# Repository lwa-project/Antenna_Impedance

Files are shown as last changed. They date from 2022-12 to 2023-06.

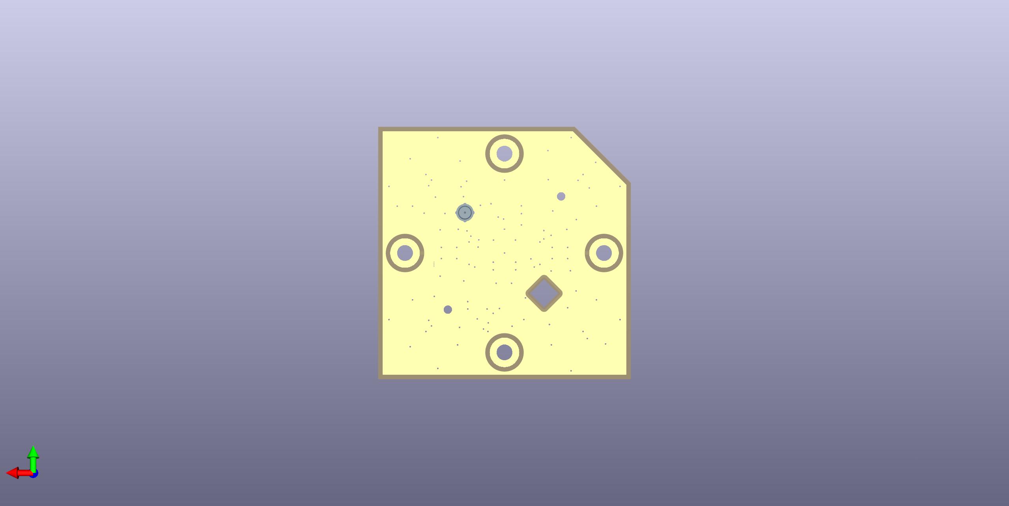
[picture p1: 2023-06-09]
Test Fixtures/LWA Active Test Fixture 2022/Output Files/3D Views/Bottom View LWA Active Test 2022.jpg

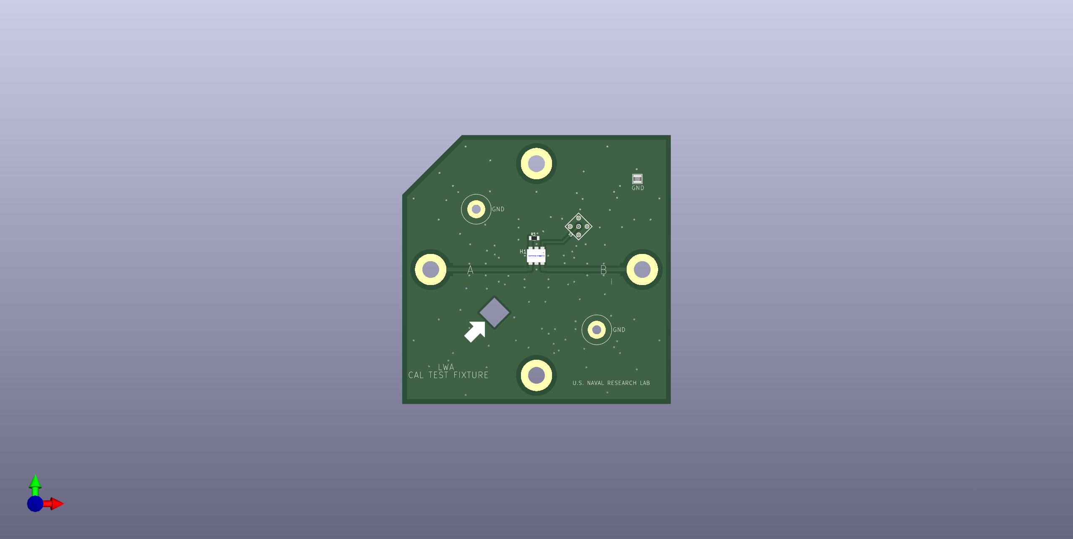
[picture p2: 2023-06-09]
Test Fixtures/LWA Active Test Fixture 2022/Output Files/3D Views/Top View LWA Active Test 2022.jpg

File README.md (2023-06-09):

Antenna_Impedance
===================
  

Description
-----------
Collection of scripts and files dealing with the LWA antenna impedance.

In the main directory are the general scripts:
* compute_IME.py: Reads in a single .s1p file containing antenna reflection coefficient data and computes the IME 
* plot_IME.py: Plots the output from computeIME.py along with the model IME from antenna simulations
* compute_IMF.py: Reads in a .npz file output by read_FEE_S_params.py and a collection of antenna .s2p files to compute the Impedance Mismatch Factor (IMF)
* plot_S_params.py: Takes in a collection of .s2p files and plots the full set of S-parameters for each antenna. Used to make the dipole-dipole measurement plots.
* plot_cross_coupling.py: Takes in a collection of .s2p files from an antenna-antenna cross coupling measurement and plots S12 and S21 for each of the four possible polarization permutations. 

Data Files
----------
In the Data/ directory there is a collection of various data files with their associated documentation.
Files include:
* BurnsZ.txt: Model IME from old antenna simulations
* A-NS_AntennaImpedance_062222.s1p: Antenna Impedance for A (N/S) polarization taken on 06/22/2022 at Whitham Reeve's house in Alaska
* B-EW_AntennaImpedance_062222.s1p: Antenna Impedance for B (E/W) polarization taken on 06/22/2022 at Whitham Reeve's house in Alaska
* A collection of dipole-dipole and antenna-antenna .s2p measurement files taken at the New Mexico stations (See "LWA_NM_Measurements_and_Procedures.pdf" for more information)

FEE
---
The Data/FEE/ directory contains:
* A collection of .s2p files which contains S-parameter measurements with the HX62A of the FEE Test Fixture de-embedded.
* read_FEE_S_params.py: A script to read both the .s1p and .s2p files and write out proper S-pramaters (S11 with HX62A de-embdedd, correct S21 and S12, and S22).
* plot_FEE_Gain.py: A script to plot the FEE Gain files which are output by read_FEE_S_params.py

Example
-------
The following is a short example which shows how to generate the IMF correction for LWA data, which requires both LWA antenna S11 measurements and FEE S11 measurements.
The FEE S11 data with the HX62A de-embedded are located in `Data/FEE/S1P/`. The single antenna measurements for each station are located in the named directories in the `Data/` directory
under `Dipole-Dipole/` (e.g. the LWA-SV measurements are in `Data/LWA-SV/Dipole-Dipole/`.

First, the FEE S-parameters with the HX62A de-embedded have to be collected into a single .npz file. To do this, use `Data/FEE/read_FEE_S_params.py` for both polarizations:
```
python3 read_FEE_S_params.py -ns S2P/*A*
```
and
```
python3 read_FEE_S_params.py -ns S2P/*B*
```
This creates two files `FEE_S11_NS.npz` and `FEE_S11_EW.npz`, respectively. Finally, to compute the IMF correction using LWA1 antenna measurements and FEE S11 measurements use `compute_IMF.py`
for each polarization via
```
python3 compute_IMF.py -ns Data/FEE/FEE_S11_NS.npz Data/LWA1/Dipole-Dipole/*
```
and
```
python3 compute_IMF.py -ns Data/FEE/FEE_S11_EW.npz Data/LWA1/Dipole-Dipole/*
```
This creates two files named `IMF_NS.txt` and `IMF_EW.txt`, respectively, which contain the IMF as a function of frequency along with the $16^{th}$ and $84^{th}$ percentile uncertainty bounds.

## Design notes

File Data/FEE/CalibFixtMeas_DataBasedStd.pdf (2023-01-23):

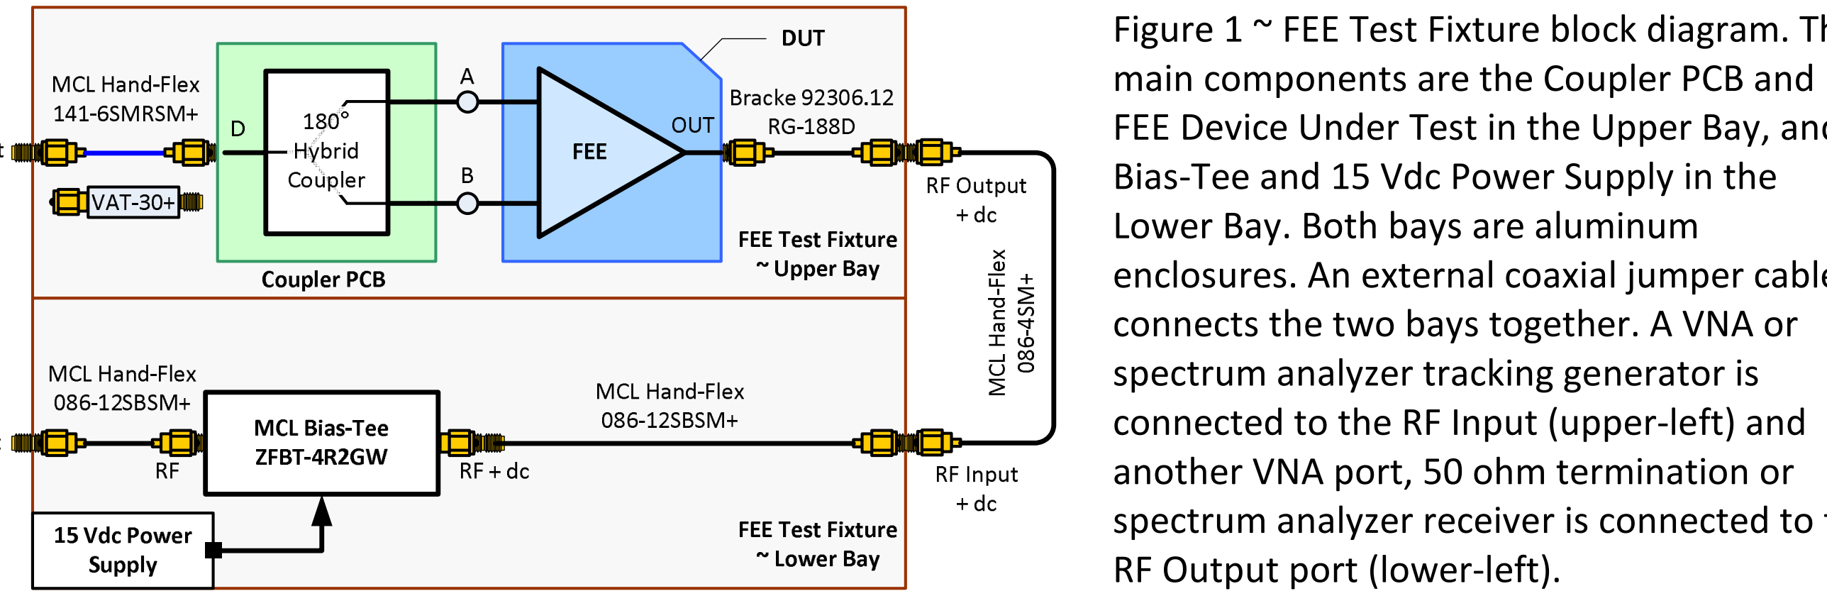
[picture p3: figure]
main components are the Coupler PCB and; Bias-Tee and 15 Vdc Power Supply in the Lower Bay. Both bays are aluminum; spectrum analyzer tracking generator is; another VNA port, 50 ohm termination or; RF Output port (lower-left).
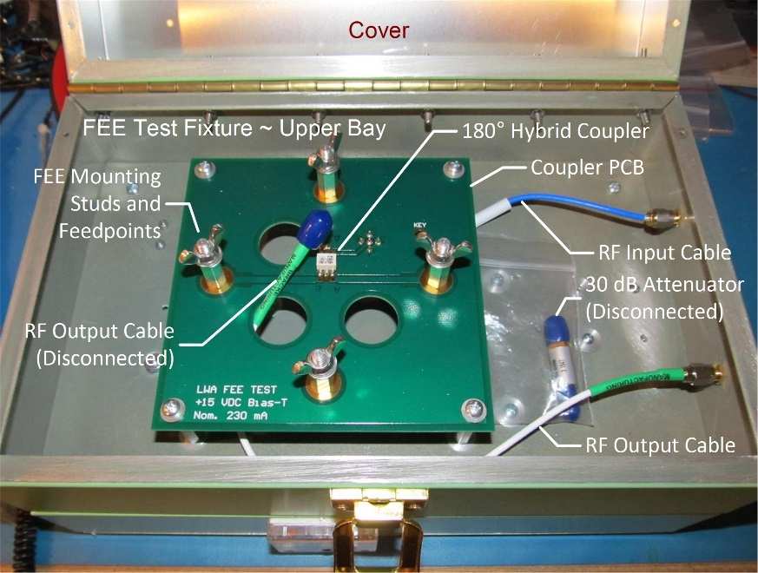
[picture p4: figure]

File: CalibFixtMeas_DataBasedStd.docx, Page 1

Calibration Fixture Measurements & Associated Data-Based Standards

The FEE Test Fixture (figures 1 and 2) is designed for measurements of the LWA Antenna Front End Electronics (FEE). To allow connection of the unbalanced 50 ohm port of a vector network analyzer (VNA) or spectrum analyzer tracking generator output to the balanced feedpoints of the FEE, the FEE Test Fixture includes a Coupler Printed Circuit Board (PCB) with a 180° hybrid coupler that provides the unbalanced to balanced transformation. Unless the hybrid coupler on the Coupler PCB is de-embedded from the measurements of the FEE, the measurements will include the characteristics of both the hybrid coupler and FEE. This paper describes using Data-Based Standards to perform the de-embedding.

The FEE Test Fixture V1 uses the HX62A hybrid coupler on the Coupler PCB, and the FEE Test Fixture V2 uses the AMT-32+ hybrid coupler on the Coupler PCB. All Calibration Fixtures use the AMT-32+ hybrid coupler. For consistency, it is necessary to use the FEE Test Fixture V2 in all measurements described below.

Figure 1 ~ FEE Test Fixture block diagram. The

FEE Device Under Test in the Upper Bay, and

enclosures. An external coaxial jumper cable connects the two bays together. A VNA or

connected to the RF Input (upper-left) and

spectrum analyzer receiver is connected to the

Figure 2.a ~ FEE Test Fixture Upper Bay showing the Coupler PCB and input and output cables. The RF Input cable connects to the difference port of the 180° hybrid coupler. The A and B ports of the hybrid coupler connect to the FEE Mounting Studs, which also serve as Feedpoints. Four studs are seen on the Coupler PCB but only the left and right studs are used during testing. The RF Output cable connects to the FEE output port. The 30 dB attenuator, shown loose in a reclosable bag, is used when measuring the FEE gain with a spectrum analyzer and tracking generator.

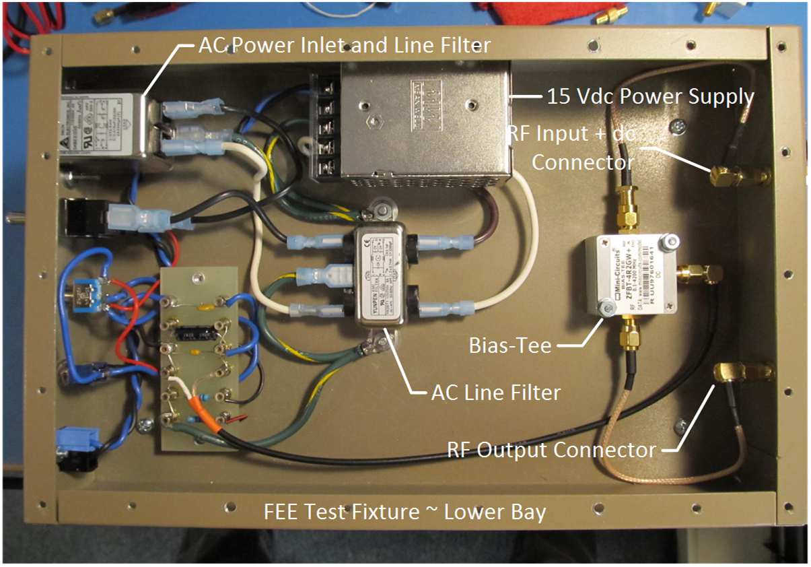
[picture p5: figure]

File: CalibFixtMeas_DataBasedStd.docx, Page 2

Figure 2.b ~ FEE Test Fixture Lower Bay showing the dc power supply, bias-tee and ac line filter components. Two stages of ac line filtering are used, and the ac power inlet is fused. Other components are current limiting resistors for the power indicating LEDs, and dc filter capacitors. The FEE Test Fixture also has selection switches for the internal or an external power source. Not visible in this image is a dc ammeter for measuring FEE load current.

VNAs are used to measure four S-parameters S11, S21, S12 and S22 but, here, we are concerned only with the S11 reflection coefficient measured at the FEE feedpoints. All VNAs require calibration prior to use. The most common VNA calibration methods involve Open, Short and Load mechanical calibration standards. A set of commercial calibration standards is called a Calibration Kit (commonly called a Cal Kit). The typical Cal Kit consists of precision coaxial devices characterized by a propagation delay term that accounts for the distance of the open or short from the reference plane of their coaxial connectors and a frequency-dependent polynomial expression that accounts for fringe capacitance in the Open and inductance in the Short standards.

The balanced feedpoint structure of the FEE consists of two annular ring pads (figure 3) that preclude connection of coaxial mechanical calibration standards, so a set of custom Open, Short and Load Calibration Fixtures was designed and fabricated (these are the same standards used for calibration in the LWA Antenna measurements). The Calibration Fixtures (figure 4) include the same type of 180° hybrid coupler and layout as the Coupler PCB described above.

The surface mount technology (SMT) resistors used in the Short and Load Calibration Fixtures are located next to the balanced feedpoints but are not connected to them. The feedpoints are transformed to the unbalanced measurement port by the hybrid coupler. The Open Calibration Fixture has no resistors (infinite resistance) but includes the hybrid coupler and empty SMT pads. Because of the hybrid coupler, the Calibration Fixtures are not easily characterized in the same terms as the commercial mechanical calibration standards described above.

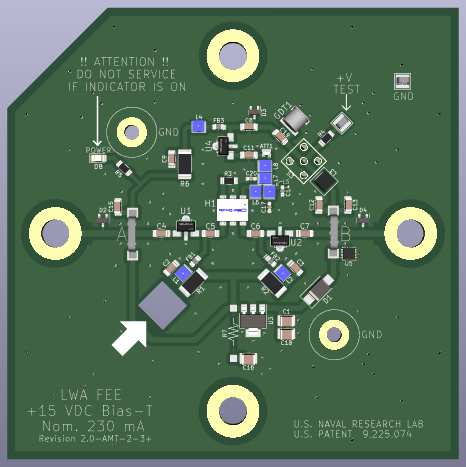
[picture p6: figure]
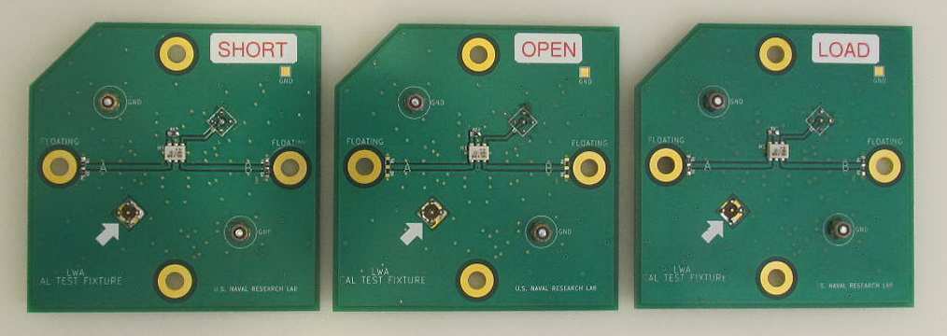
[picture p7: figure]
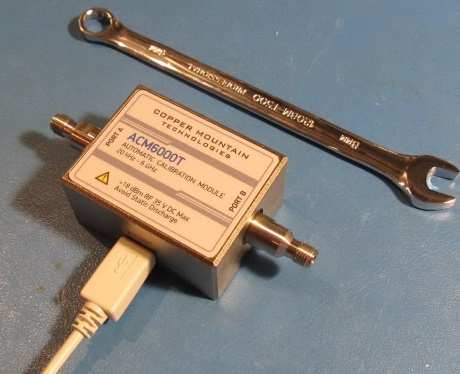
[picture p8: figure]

File: CalibFixtMeas_DataBasedStd.docx, Page 3

Figure 3 ~ CAD image of the FEE. Dimensions are 4.5 x 4.5 in (114.3 x 114.3 mm). The FEE consists of two identical PCBs except for the direction of the SMA connector (the connector pads are seen near the middle of the upper-right quadrant). The PCBs are sandwiched back-to-back to provide a dual assembly. The left and right annular rings are connected to circuitry facing out of the page and the upper and lower annular rings are connected to the circuitry on the other PCB facing into the page. The ring hole diameters are slightly more than ¼ in (6.35 mm). During normal operation, the FEE is mounted to studs in the LWA Antenna central hub. The corner notch (upper-left) ensures proper alignment in the antenna hub. For test purposes, the FEE is mounted in the FEE Test Fixture, which has an identical stud layout that provides connections to the Coupler PCB.

Figure 4 ~ Calibration
Fixtures. Each fixture is a dual assembly of two
identical PCBs. The SMT
pads for the Short and Load resistors are adjacent to the annular rings. The Open
Fixture has pads but no
resistors. All use the AMT-32+ hybrid coupler.

An alternative characterization method involves carefully measuring the S11 reflection coefficients of the Calibration Fixtures and then using those measurements as Data-Base Standards for VNA calibration. In this method, the VNA is used to measure the reflection coefficient of each Calibration Fixture. Ideally, the data base is created by measurements with a metrology-grade VNA that has been calibrated with primary standards in a controlled environment laboratory. As a practical matter, the measurements can be made with a high-quality VNA after it has been calibrated with an Automatic Calibration Module (ACM) (figure 5).

Figure 5 ~ Copper Mountain Technologies USB-controlled ACM6000T-111 Automatic Calibration Module with two ports and SMA-female connectors shown adjacent to an 8 mm wrench. The ACM allows more precise VNA calibration than a mechanical Cal Kit. The device is controlled through a USB port and provides Short, Open, Load and Thru standards in one small package.

The measurement data includes the embedded hybrid coupler in the Calibration Fixtures, which, by proxy, includes the embedded hybrid coupler on the FEE Test Fixture Coupler PCB. This method assumes that the electrical differences between the hybrid couplers used in the Calibration Fixtures and the hybrid coupler in the Coupler PCB are negligible. The Calibration Fixtures and their associated measurement data are then used to

File: CalibFixtMeas_DataBasedStd.docx, Page 4 recalibrate the VNA before measuring an FEE, thus moving the measurement reference plane from the VNA port to the balanced feedpoints of the FEE in the FEE Test Fixture.

The ACM includes the Open, Short, Load, and Through standards in one unit and is controlled by the VNA through a USB port. One advantage of an ACM is that it is individually characterized at the factory, including thermal modeling, allowing more precise VNA calibration than normally possible with mechanical calibration standards. Although mechanical standards are precision devices, they normally are not individually characterized or thermally modeled as is the ACM. The same delays and polynomial coefficients apply to thousands of mechanical calibration standards with the same part number, and the uncertainties in these parameters are unavoidably higher than in an ACM.

Calibration Fixture Data Base Measurements

The Copper Mountain Technologies (CMT) M5045 Vector Network Analyzer and CMT ACM6000T-111 Automatic Calibration Module are used to measure the Calibration Fixtures. The same cable arrangement is used during VNA calibration with the ACM and during measurements of the Calibration Fixtures; thus, the cables are calibrated out. The VNA is setup with the start and stop frequency, number of measurement points, and IF bandwidth. The ACM is automatically detected when the ACM has been connected to a PC USB port.

The ACM is installed at the end of the VNA Test Cable Arrangement on port 1 and a 50 ohm termination is connected to the unused ACM port. A Full 1-Port calibration is initiated. The Test Cable Arrangement includes a 1 m long Test Cable from the VNA and a 6 in long Jumper Cable that is the proxy for the internal RF Input Jumper Cable inside the FEE Test Fixture. This establishes the calibration reference plane at the end of the Test Cable Arrangement. When the automatic calibration has finished, the Calibration Fixtures are installed one by one at the end of the Test Cable Arrangement (figure 6). The S11 parameter measurements are saved as S1P Touchstone files, one each for the Side A Open, Short and Load Calibration Fixtures. The measurements are then repeated for the Side B Open, Short and Load Calibration Fixtures. Two sets of Calibration Fixtures have been constructed and marked with a Red or Yellow dot. All measurements are repeated for both sets of Calibration Fixtures.

The Define STD Data and Define STD CLS functions in the VNA software are then used to define a Data-Based Open, Short and Load from the S1P data files obtained above. Four sets of definitions, or Cal Kits, are produced, one each for Side A and Side B of the Red and Yellow Calibration Fixtures. The definitions are saved to the list of calibration kits available in the VNA. Now, when the VNA is calibrated with these Cal Kits, the hybrid coupler and cables are de-embedded and the measurement reference plane is at the balanced feedpoint of the FEE installed in the FEE Test Fixture.

Several sets of measurements were made to 1) check for hand-capacitance effects, 2) determine if the Calibration Fixtures may be placed on the outside of the FEE Test Fixture and 3) determine if the RF Input Jumper Cable in the FEE Test Fixture may be temporarily replaced with a separate but identical Jumper Cable. Placing the Calibration Fixtures outside the FEE Test Fixture and using an external Jumper Cable minimizes the mechanical disassembly and reassembly of the FEE Test Fixture during the several steps of calibration and FEE measurements. The only hand capacitance effects observed were when the exposed pads or component leads on the Calibration Fixtures were physically touched while holding the fixture, which is not done during

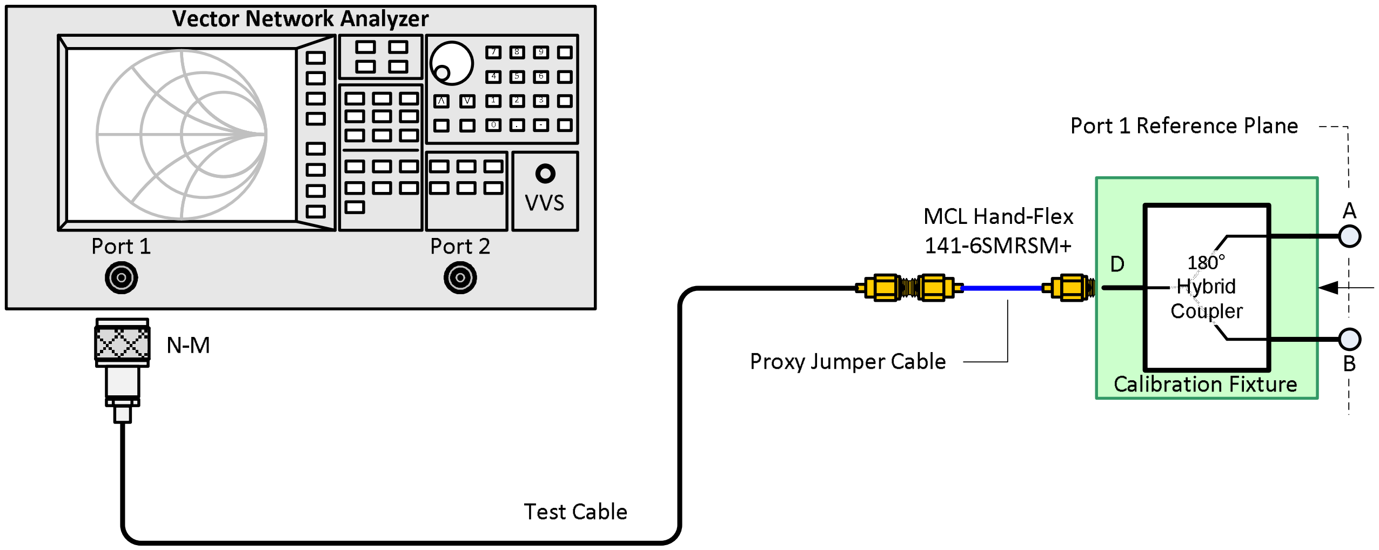
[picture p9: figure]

File: CalibFixtMeas_DataBasedStd.docx, Page 5 calibration or measurements. Also, there were no differences observed between setting the Calibration Fixtures in the FEE Test Fixture and setting them on the test bench external to the FEE Test Fixture with the proxy Jumper Cable.

Figure 6 ~ Calibration setup diagram for Calibration Fixture measurements. Measurements have demonstrated that the Calibration Fixtures may be set outside of the FEE Test Fixture during VNA calibration to minimize mechanical disassembly and reassembly of the FEE Test Fixture. The MCL 141-6SMRSM+ Jumper Cable used in calibration is a proxy for an identical cable used in the FEE Test Fixture.

Procedures:

These procedures produce the data necessary for defining Calibration Fixture Data-Based Standards. These standards apply only to the frequency range 5 to 200 MHz and with an MCL ULC-1M-SMNM+ Test Cable and MCL 141-6SMRSM+ Jumper Cable. Four Cal Kits are produced: Red-A, Red-B, Yellow-A, and Yellow-B:

Step 1 – Initial VNA Calibration:

### 1. Connect the VNA Port 1 Test Cable to the proxy RF Input Jumper Cable (MCL 141-6SMRSM+)

Notes:
a. The proxy cable includes an SMA-female coupler on one end and SMA-male right-angle connector on the other end (same as in the FEE Test Fixture);
b. The combination of the Test Cable and proxy cable is called Test Cable Arrangement

### 2. Setup the VNA for frequencies, number of measurement points and IF bandwidth

3. Connect the ACM Port A to the Test Cable Arrangement and Port B to a 50 ohm termination

### 4. Select AutoCal 1-Port AutoCal (AutoCal is initiated)

### 5. After calibration has finished, the calibration is applied automatically

Step 2 – Measure S11 reflection coefficient of the Calibration Fixtures. This step is required for each of the three Calibration Fixtures:
1. Connect Side A of the Yellow Dot Open Calibration Fixture to the Test Cable Arrangement

### 2. Terminate Side B of the Yellow Dot Open Calibration Fixture with a 50 ohm termination

### 3. Measure 1-Port S11 reflection coefficient on VNA Port 1

### 4. Save measurements as S1P and PNG files

### 5. Repeat steps 1 through 4 for Side B of the Yellow Dot Open Calibration Fixture

### 6. Repeat steps 1 through 5 for Side A and B of the Yellow Dot Short Calibration Fixture

File: CalibFixtMeas_DataBasedStd.docx, Page 6

### 7. Repeat steps 1 through 5 for Side A and B of the Yellow Dot Load Calibration Fixture

### 8. Repeat steps 1 through 7 for the Red Dot Open, Short and Load Calibration Fixtures

Step 3 – Prepare Data-Based Standards for the Calibration Fixtures:
1. Using the S11 measurements of the Open, Short and Load for each set, prepare four Data-Based Standards Cal Kits
2. Define STDs Open, Short and Load, one set of each for Side A and Side B of the Red Dot Calibration Fixtures and one set of each for Side A and Side B of the Yellow Dot Calibration Fixtures

### 3. Define CLSs, Open -F-, Short -F- and Load -F-

File: CalibFixtMeas_DataBasedStd.docx, Page 7

Document Information
Author: Whitham D. Reeve
Revisions: 0.0 (Original draft started, 07 Jan 2023) 0.1 (Major edits, 08 Jan 2023)
0.2 (Updates per tests, 18 Jan 2023) 0.3 (Edited procedures, 19 Jan 2023) 0.4 (Replaced ACM image, 20 Jan 2023) 0.5 (Record, 21 Jan 2023)

Word count: 2892
File size (bytes): 1927712

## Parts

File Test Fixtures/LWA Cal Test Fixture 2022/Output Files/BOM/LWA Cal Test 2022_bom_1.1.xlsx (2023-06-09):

Component | References | MFGR | MPN | Value | Desc | Footprint | Quantity Required | Stock | Stock Date | Tolerance | Unit Cost | Extended
1 | H1 | Mini-Circuits | AMT-32+ | AMT-32+ | Magic Tee, 50 - 200 MHz, 180 deg Hybrid, 50Ω | AMT-2 | 16 | 66 | 03/03/2022 | NA | $13.45 | $215.20
2 | R3 | Vishay Foil Resistors | Y162550R0000B9W | 50R | RES SMD 50 OHM 0.1% 0.3W 1206 | R_1206_3216Metric_Pad1.30x1.75mm_HandSolder | 1 | 2007 | 04/26/2022 | 0.1% | $0.56 | $0.56
3 | R1 R2 R4 R5 | YAGEO | RC1206FR-07100RL | 100R | RES 100 OHM 1% 1/4W 1206 | R_Cal_1206 | 100 | 2220743 | 04/24/2022 | 1% | $0.03 | $3.00
4 | R1 R2 R4 R5 | YAGEO | RC1206JR-070RL | 0R (Shunt) | RES 0 OHM JUMPER 1/4W 1206 | R_Cal_1206 | 100 | 2220743 | 04/24/2022 | NA | $0.02 | $2.00
5 | S3 | Cinch Connectivity Solutions Johnson | 142-0701-201 | TEST | CONN SMA JACK STR 50 OHM PCB | SMA_142-0701-201 | 20 | 40347 | 03/03/2022 | NA | $4.94 | $98.80
6 | TP2 | Harwin Inc | S1751-46R | GND TEST | PC TEST POINT NATURAL | Harwin_TP_S1751-46R | 100 | 157264 | 03/03/2022 | NA | $0.20 | $20.00
 |  |  |  |  |  |  |  |  |  | Total Parts Cost: |  | $339.56
Note: This BOM covers deliverable components needed for both sets of boards.

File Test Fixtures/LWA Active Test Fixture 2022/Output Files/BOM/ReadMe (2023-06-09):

Please see other Project 'LWA Cal Test 2022' for procurement BOM.

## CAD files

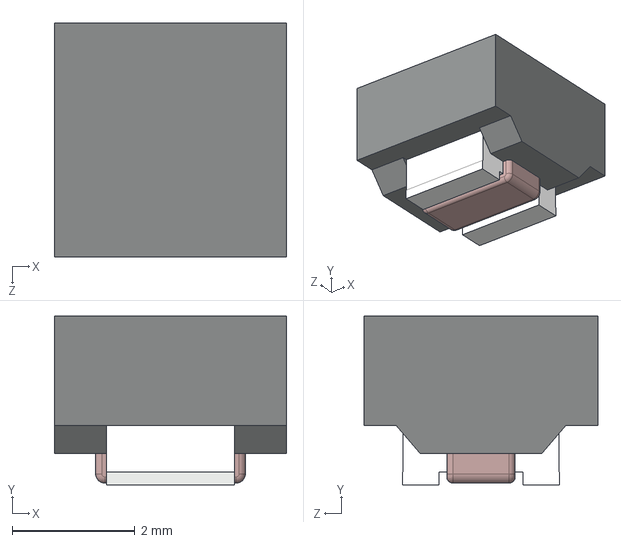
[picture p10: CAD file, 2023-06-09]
Test Fixtures/LWA Active Test Fixture 2022/3D Models/Coilcraft-1008PS.STEP
3.78 x 2.75 x 3.81 mm

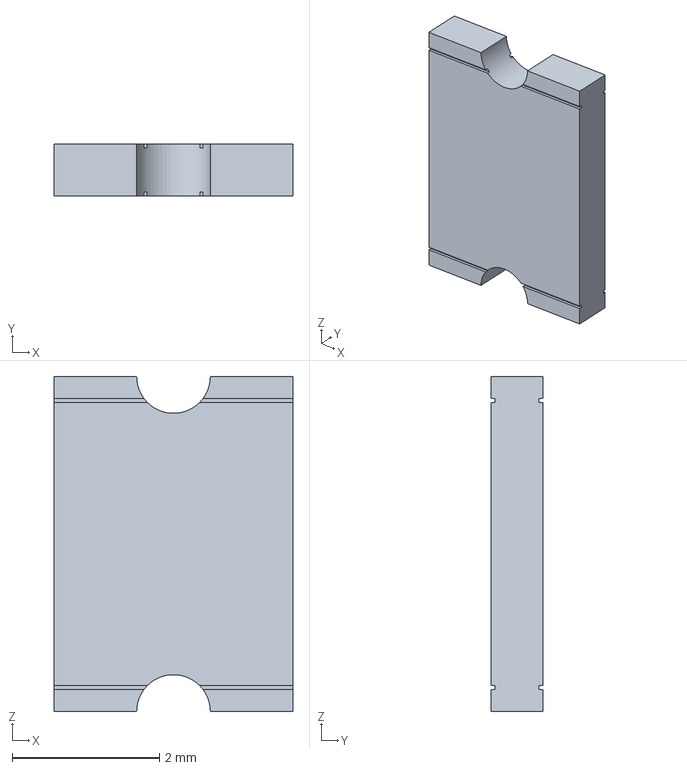
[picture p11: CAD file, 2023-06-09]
Test Fixtures/LWA Active Test Fixture 2022/Project PCB Libraries/3D Models/mf-msmf050.stp
3.24 x 0.7 x 4.55 mm

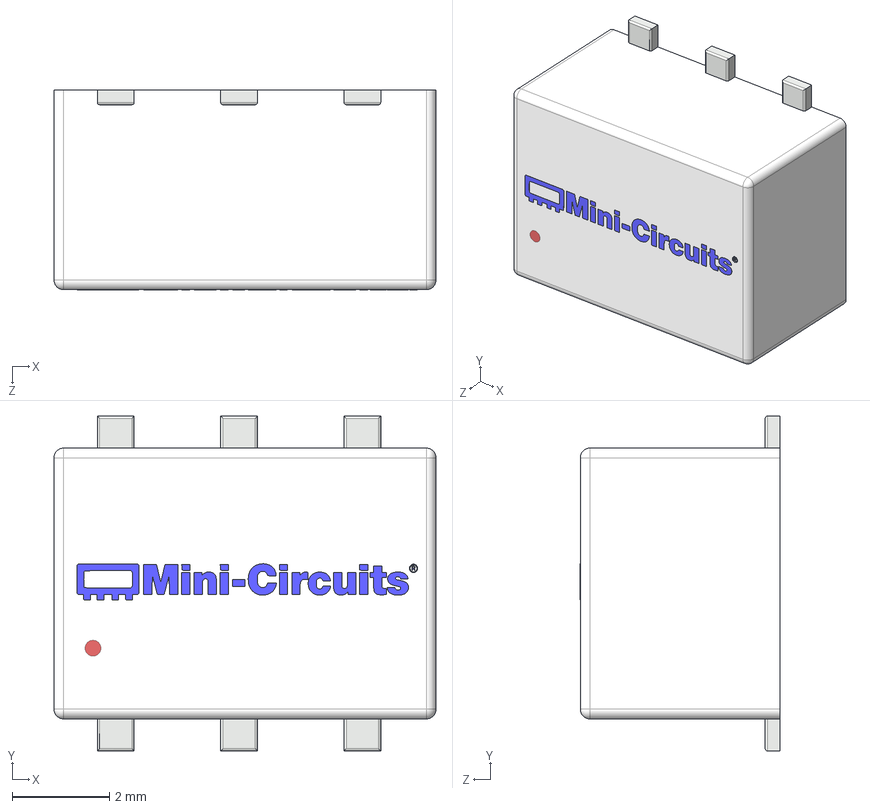
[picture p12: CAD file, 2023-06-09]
Test Fixtures/LWA Cal Test Fixture 2022/3D Models/CD636-1.STEP
7.87 x 6.90 x 4.11 mm

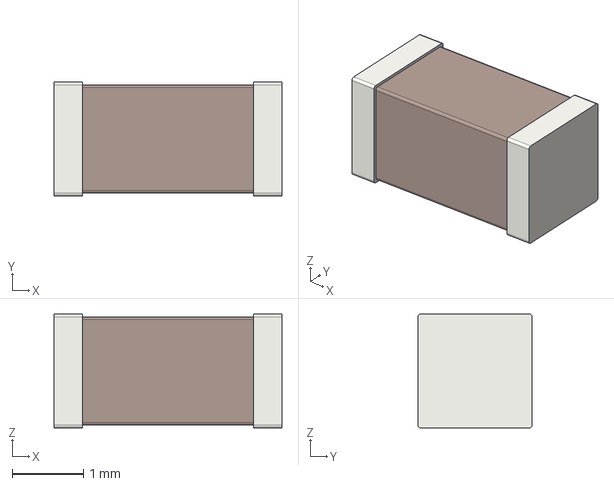
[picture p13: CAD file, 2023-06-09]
Test Fixtures/LWA Cal Test Fixture 2022/Project PCB Libraries/3D Models/C_1206_3216Metric.step
3.20 x 1.60 x 1.60 mm

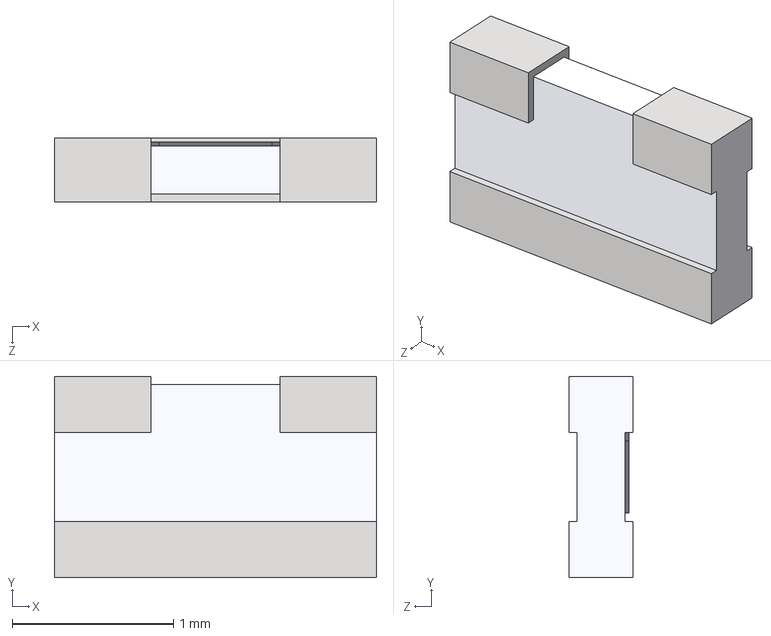
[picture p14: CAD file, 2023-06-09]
Test Fixtures/LWA Active Test Fixture 2022/3D Models/PAT1210.STEP
2.00 x 1.25 x 0.4 mm

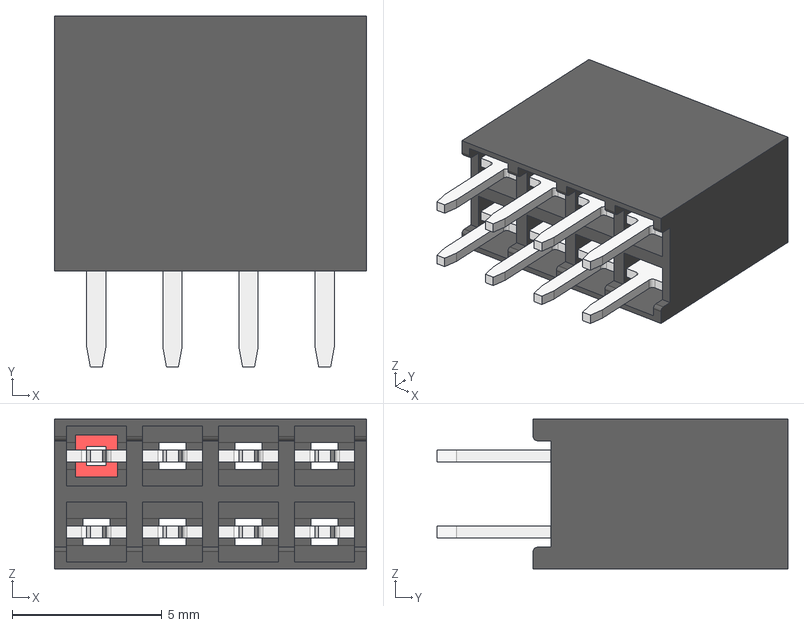
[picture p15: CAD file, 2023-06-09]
Test Fixtures/LWA Active Test Fixture 2022/Project PCB Libraries/3D Models/Female Header 2x4_2.54 mm.stp
10.4 x 11.7 x 5.00 mm

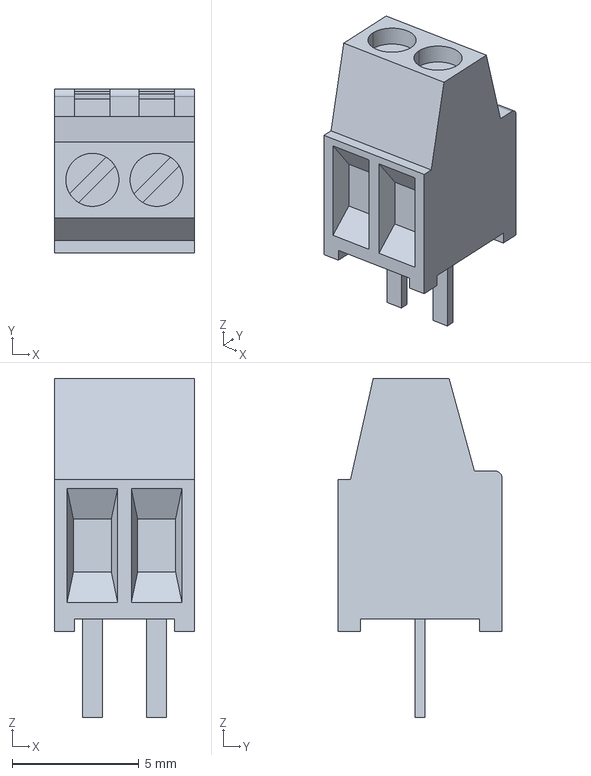
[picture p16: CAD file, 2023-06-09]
Test Fixtures/LWA Cal Test Fixture 2022/Project PCB Libraries/3D Models/Terminal 282834-2-c-3d.stp
5.54 x 6.50 x 13.4 mm

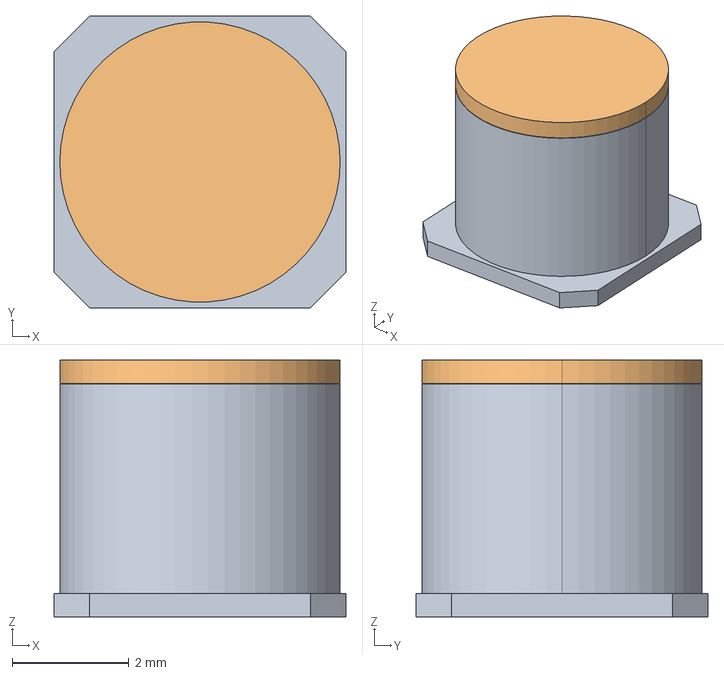
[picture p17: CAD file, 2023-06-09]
Test Fixtures/LWA Active Test Fixture 2022/3D Models/2035-09-sm-rplf.stp
5.00 x 5.00 x 4.40 mm

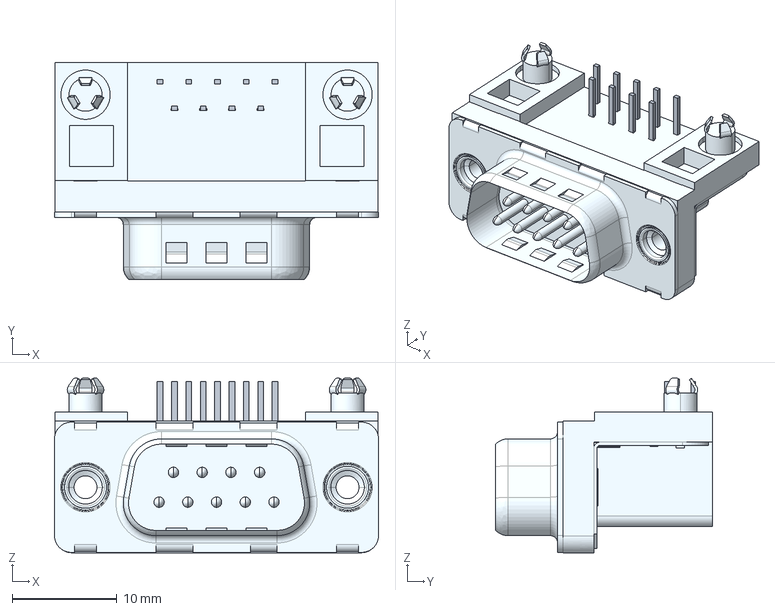
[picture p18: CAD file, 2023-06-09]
Test Fixtures/LWA Active Test Fixture 2022/Project PCB Libraries/3D Models/DB9M.stp
30.9 x 20.7 x 16.6 mm

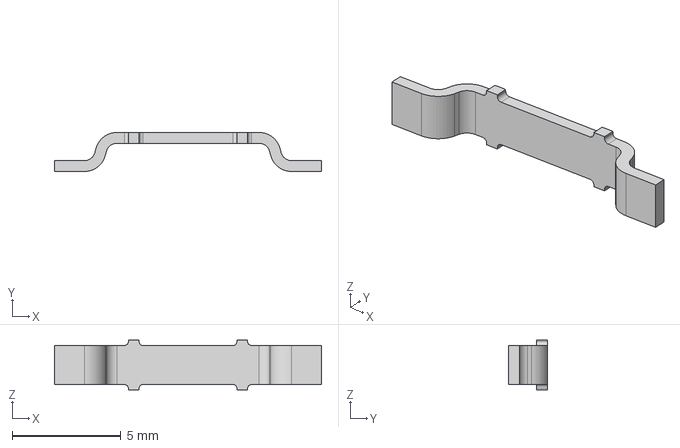
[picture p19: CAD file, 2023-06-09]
Test Fixtures/LWA Cal Test Fixture 2022/3D Models/s1621-46r.stp
12.3 x 1.80 x 2.30 mm

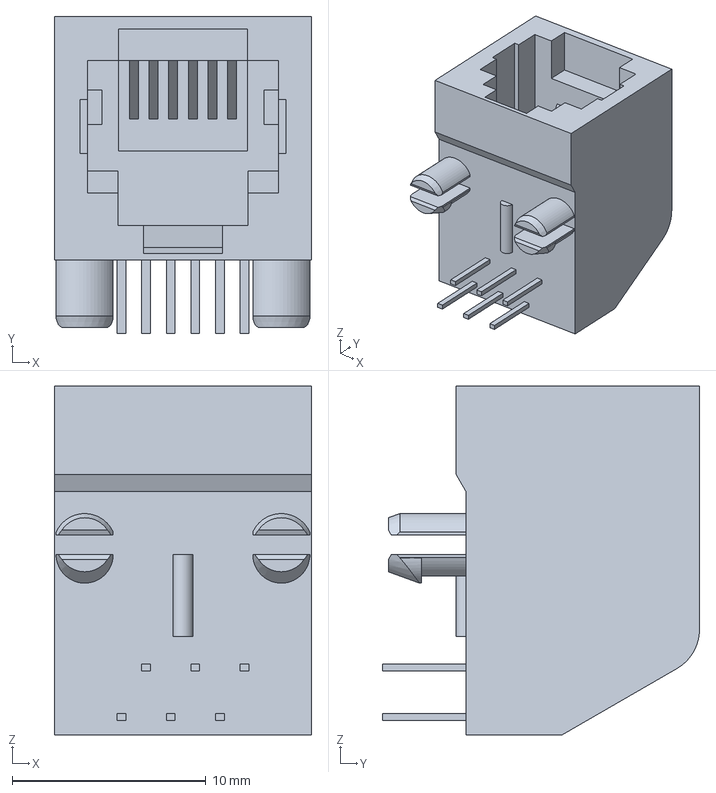
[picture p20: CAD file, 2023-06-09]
Test Fixtures/LWA Cal Test Fixture 2022/Project PCB Libraries/3D Models/c-5555165-1-e-3d.stp
13.3 x 16.4 x 18.0 mm

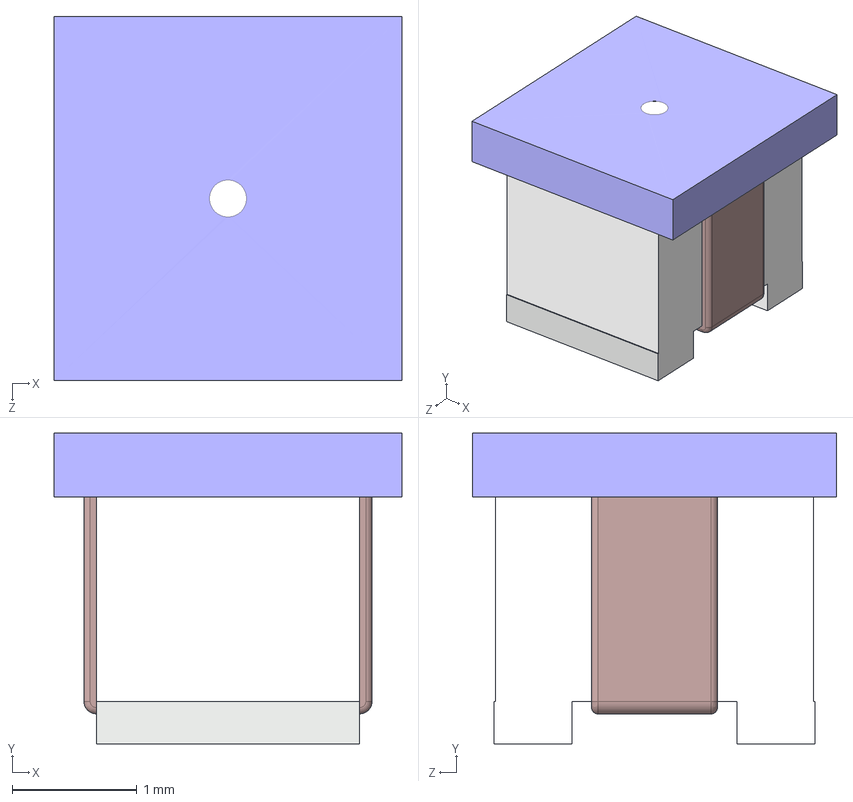
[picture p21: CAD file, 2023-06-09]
Test Fixtures/LWA Active Test Fixture 2022/3D Models/Coilcraft-1008CS.STEP
2.79 x 2.49 x 2.92 mm

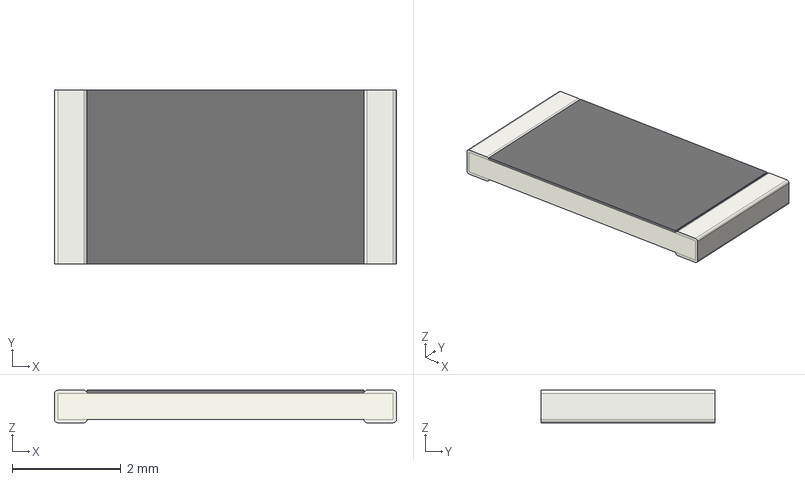
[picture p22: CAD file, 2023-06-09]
Test Fixtures/LWA Active Test Fixture 2022/Project PCB Libraries/3D Models/R_2512_6332Metric.step
6.30 x 3.20 x 0.6 mm

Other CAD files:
Test Fixtures/LWA Active Test Fixture 2022/3D Models/142-0701-201.stp
Test Fixtures/LWA Active Test Fixture 2022/Project PCB Libraries/3D Models/459120007.stp
Test Fixtures/LWA Active Test Fixture 2022/Project PCB Libraries/3D Models/CUI_CVS-1508.step
Test Fixtures/LWA Active Test Fixture 2022/Project PCB Libraries/3D Models/HC49_US-SM.STEP
Test Fixtures/LWA Active Test Fixture 2022/Project PCB Libraries/3D Models/Micro_USB_A_10103594.STEP
Test Fixtures/LWA Active Test Fixture 2022/Project PCB Libraries/3D Models/PT10xV10-A_w_axle-1.STEP
Test Fixtures/LWA Active Test Fixture 2022/Project PCB Libraries/3D Models/keystone-PN3034TR.STEP
Test Fixtures/LWA Cal Test Fixture 2022/3D Models/142-0701-201.stp
Test Fixtures/LWA Cal Test Fixture 2022/Project PCB Libraries/3D Models/459120007.stp
Test Fixtures/LWA Cal Test Fixture 2022/Project PCB Libraries/3D Models/CUI_CVS-1508.step
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

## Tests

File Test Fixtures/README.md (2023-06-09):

Test Fixtures
=============

Description
-----------
This directory contains the KiCAD v7 project files needed to build the test
fixtures used in [DiLullo et al. (2023, PASP)](https://arxiv.org/abs/2303.14904).
There are two sub-directories: "LWA Active Test Fixture 2022" and "LWA Cal Test
Fixture 2022".  "Active" contains the board that was used to make the impedance
measurements.  "Cal" contains the base board for making the open,
short, and load calibration fixtures for the measurements.

Within each sub-directory is the full KiCAD v7 project, the Gerber files, and BoM
for the board, relevant data sheets for the parts used, and an image of the
rendered 3D model of the full board.

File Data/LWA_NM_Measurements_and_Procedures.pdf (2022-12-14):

LWA Antenna Measurement Procedures

File: LWA Ant Meas Proc.docx, Page 1

### 0. General:

a. These procedures describe impedance and coupling measurements of the LWA Antenna dipoles using the FieldFox N9917A Microwave Analyzer. The FieldFox is equipped with a GPS receiver so its location may be recorded. The measurement frequency range is 5 to 200 MHz.
b. Two measurement configurations are described:
1) Individual antenna measurements including dipole impedance and dipole-dipole coupling. This configuration requires one Antenna Test Fixture and two Test Cables. Refer to Diagram 0.1 and section 2. Measurements for each antenna are:
S11: Dipole A impedance (reflection coefficient)
S21: Dipole A to Dipole B coupling (transmission coefficient)
S12: Dipole B to Dipole A coupling (transmission coefficient)
S22: Dipole B impedance (reflection coefficient)
2) Antenna measurements including dipole impedance and antenna-antenna coupling. A complete set of measurements for an antenna pair (four dipoles) includes four setups, where X is one antenna with dipoles A and B and Y is another antenna with dipoles A and B. This configuration requires two Antenna Test Fixtures and four Test Cables. Refer to Diagram 0.2 and section 3. Measurements for each antenna pair are:
S11: Antenna X, Dipole A reflection coefficient
S21: Antenna X, Dipole A to Antenna Y, Dipole B transmission coefficient
S12: Antenna Y, Dipole B to Antenna X, Dipole A transmission coefficient S22: Antenna Y, Dipole B reflection coefficient
c. All calibrations and measurements use the dual assembly v2 Calibration Fixtures (standards) and Antenna Test Fixtures. In addition to the Open, Short and Load Calibration Fixtures (standards), an Unknown Thru calibration standard is required. The Unknown Thru consists of an Antenna Test Fixture dual assembly, split apart and connected back-to-back through steel spacers with the SMA connectors pointed outward. For the Thru calibrations, the Test Fixture PCBs are connected in-phase (Feedpoint A on one PCB to Feedpoint A on the other PCB).
d. The Calibration and Test Fixtures are mounted using all four studs (feedpoints) in the antenna central hub. For reference, Fixture Side A is the Side facing up and Fixture Side B is the Side facing down when mounted on the antenna.
e. The instrument calibration protocol is as follows: Calibrate at the beginning of each measurement day. Recalibrate if the analyzer internal temperature changes by ≥ 5 °C (10 °F) from the initial calibration. Recalibrate if any of the following are changed after initial calibration: Frequency range; Output Power; IF Bandwidth; or Resolution. Note: These procedures may require changing IF Bandwidth to improve trace and measurement quality.
f. The analyzer should be shaded and kept out of direct sunlight whenever possible, and RF connectors protected from dust at all times with caps or tape. Connectors must be clean of contamination before connecting.

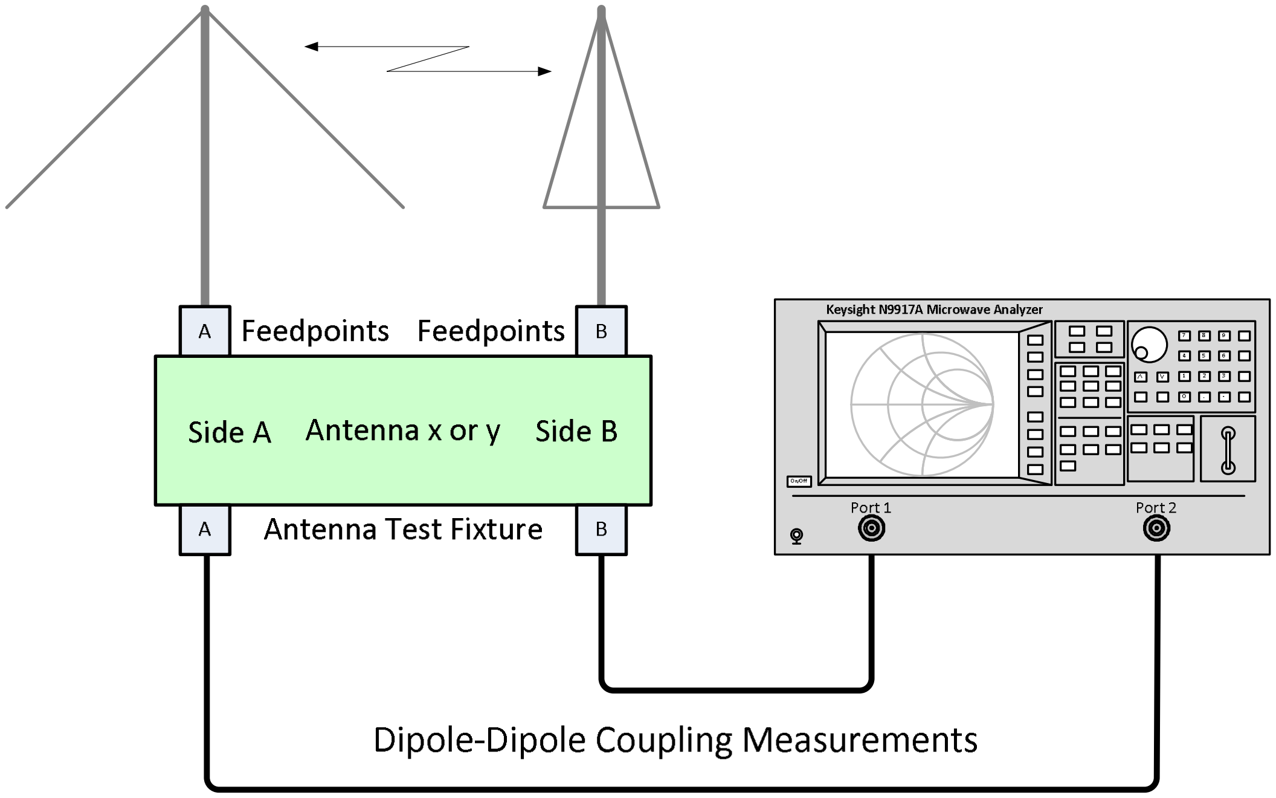
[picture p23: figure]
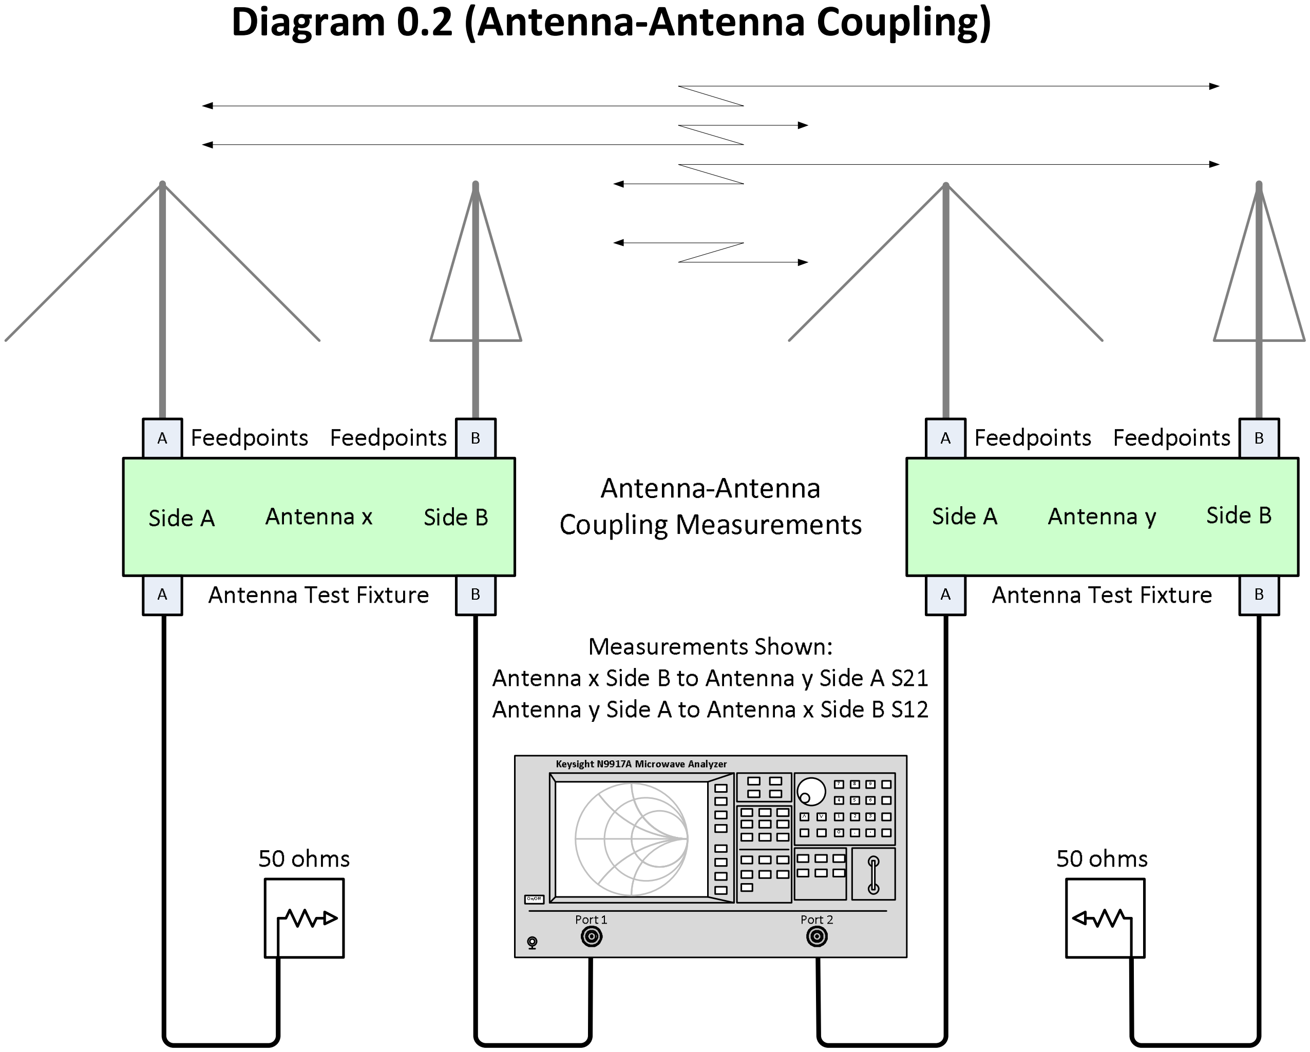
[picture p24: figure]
Diagram 0.2 (Antenna-Antenna Coupling)

File: LWA Ant Meas Proc.docx, Page 2

Diagram 0.1 (Dipole Impedance & Dipole-Dipole Coupling)

### 1.0. Preliminary:

a. Log the antenna stand number (AN) and location of each measured antenna (log will be used as a filename crosscheck).
b. When saving data and screen images, include the stand number in the filename.
c. For all measurements in section 1, S11 is dipole A impedance, S21 is dipole A to B coupling, S12 is dipole B to A coupling, and S22 is dipole B impdedance.
d. When measuring an LWA Antenna, the FieldFox internal GPS receiver may be used for location but the recorded location will be for the GPS antenna and not the LWA Antenna being measured. When using the GPS receiver, watch battery consumption.
e. Test equipment:

File: LWA Ant Meas Proc.docx, Page 3

1) Vector Network Analyzer: N9917A FieldFox Microwave Analyzer
2) Calibration Fixtures (standards) for Short, Open, Load and Unknown Thru: Version 2, consisting of dual assembly PCBs
3) Antenna Test Fixture: Version 2 consisting of dual assembly PCBs, (2) required
4) Test Cable RED (X): N-M – SMA-M, LMR-240, 37 ft (11 m) long
5) Test Cable GREEN (X): N-M – SMA-M, LMR-240, 37 ft (11 m) long
6) Test Cable RED-RED (Y): N-M – SMA-M, LMR-240, 37 ft (11 m) long
7) Test Cable GREEN-GREEN (Y): N-M – SMA-M, LMR-240, 37 ft (11 m) long
8) 50 ohm termination: N-F, Maury Microwave 2510B1 (alt. N-M, MCL KARN-50+ with coaxial coupler, N-F/N-F, UG-29A/U), (2) required
9) Torque wrench: 5/16 in, 5 in-lb, Fairview Microwave NC-100, ST-SMA5
10) GPS antenna: 3-5 V, 3 m cable, SMA-M connector
11) Test set status as of 16 October 2022:
Mfr | Type | S/N | Cal due
Keysight | N9917A FieldFox, FW A.12.46 | MY56071016 | 23 Dec 2023
Agilent | 85033D 3.5 mm Cal Kit | 3423A05729 | 15 Jul 2024
Saluki Tech | SCK0YTL26.5-3.5-F Cal Kit | WBG01482 | 21 Aug 2023

### 2.0. Antenna impedance and dipole-dipole coupling measurements:

a. Dipole impedance is measured in terms of dB and angle as reflection coefficients S11 for Dipole A and S22 for Dipole B.
b. Dipole-dipole coupling is measured in terms of dB and angle as transmission coefficients S21 for Dipole A to Dipole B and S12 for Dipole B to Dipole A.
c. Two 37 ft (11 m) Test Cables are used to physically isolate the network analyzer (NA) from the antenna under test. The Test Cables are placed as close as possible in line with the existing antenna cables.
d. It is expected that dipole-dipole coupling will be low, so it will be necessary to use the High Output power setting in the NA. This is typically –2 dBm for the FieldFox at the frequencies of interest.
e. To reduce trace noise on the dipole-dipole coupling measurements, it may be necessary to experiment with IF Bandwidth and Averaging for best S21 and S12 traces. Changing the IF bandwidth requires a new calibration.
f. During calibration and measurements, the near ends of the Test Cables are connected to the NA Port 1 and Port 2. The far ends of the cables are connected to the Calibration Fixtures and Antenna Test Fixture at the Antenna Under Test (AUT).
g. A Full 2-port calibration is used. With the FieldFox, it is necessary to calibrate Port 1 with the Open, Short and Load Calibration Fixtures and then Port 2 with the Open, Short and Load Calibration Fixtures in the specific order shown by the instrument display prompts. An Unknown Thru is used to connect Port 1 to Port 2 in the last calibration step.
h. The LWA Ideal Cal Kit 200MHz parameter declarations file (already loaded in the FieldFox) is used for NA calibration with the Calibration Fixtures; this calibration file assumes the Calibration Fixtures are ideal (zero coefficients and zero delay).

File: LWA Ant Meas Proc.docx, Page 4

### 2.1. Setup for calibration of dipole impedance and dipole-dipole coupling measurements:

1) Setup Analyzer mode:
☐ | Mode NA
☐ | Mode Preset (factory)
2) Setup Traces:
☐ | Trace x4
☐ | Trace 1 Measure S11 Log Mag
☐ | Trace 2 Measure S21 Log Mag
☐ | Trace 3 Measure S12 Log Mag
☐ | Trace 4 Measure S22 Log Mag
3) Setup Frequency & Amplitude scale:
☐ | Freq/Dist Start 5.0 MHz, Stop 200.0 MHz
☐ | Scale/Amptd Scale 5 dB or 10 dB as required
☐ | Scale/Amptd Ref Level 0 dB
☐ | Scale/Amptd Ref Pos 5
4) Check IF bandwidth and averaging:
☐ | BW IF BW 10 kHz (may require adjustment depending on results, recalibration required)
☐ | BW Average <n> 1 Enter (may require adjustment depending on results)
☐ | BW Average Mode Sweep
☐ | To restart Sweep, go to Sweep Restart
5) Measure setup:
☐ Meas Setup Output power High
6) Setup Sweep:
☐ Sweep Resolution More 1001 Enter Back (resolution 195.0 kHz)
7) Setup Markers:
☐ | Mrkr 1 Normal 5 MHz
☐ | Mrkr 2 Normal 10 MHz
☐ | Mrkr 3 Normal 20 MHz
☐ | Mrkr 4 Normal 40 MHz
☐ | Mrkr 5 Normal 80 MHz
☐ | Mrkr 6 Normal 160 MHz
☐ | Mrkr Table: ON
8) Connections for calibration:
☐ | Refer to Diagram 2.1 below
☐ | Connect Test Cables to Calibration Fixture and install Calibration Fixture on Hub of AUT: Test
| Cable RED to Side A and Test Cable GREEN to Side B
☐ | Connect NA Port 1 to Test Cable A (RED) and NA Port 2 to Test Cable B (GREEN)
9) Calibration:
☐ | Cal Mechanical Cal Change DUT Connectors SMA Change Gender Female
| Next Port 2 SMA Change Gender Female Next

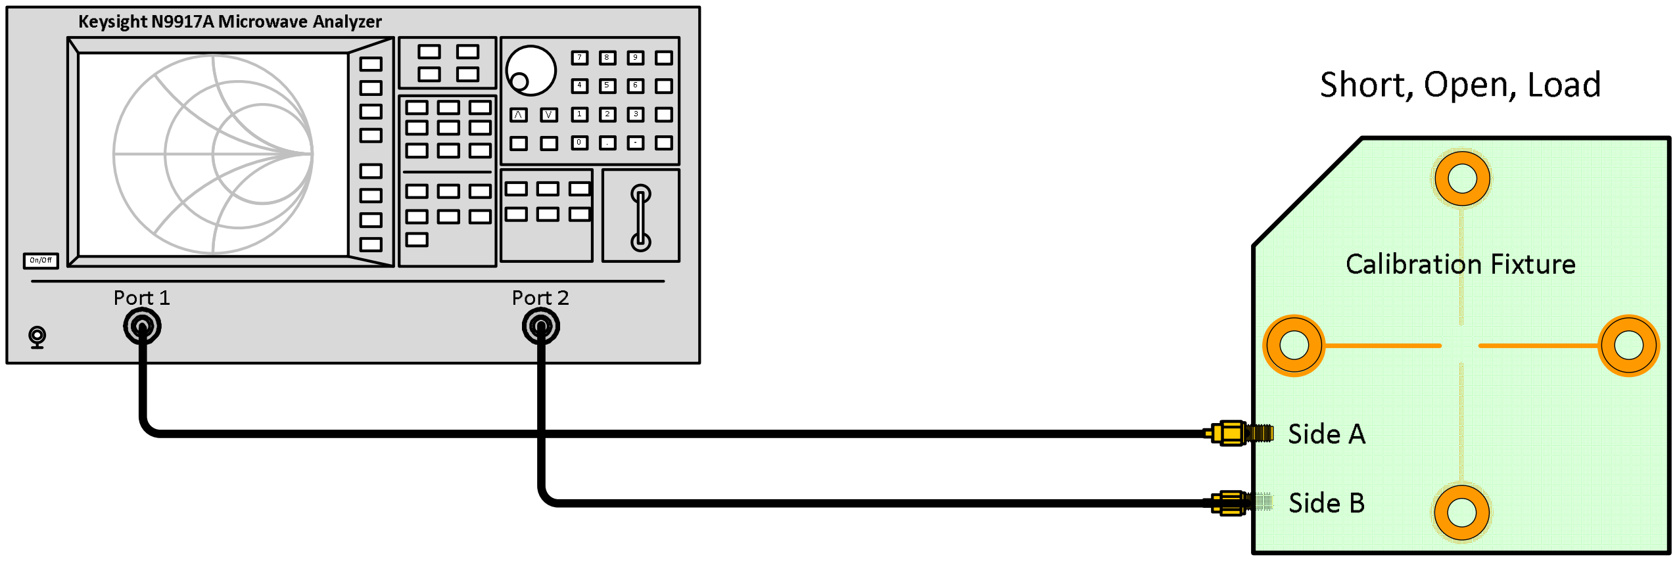
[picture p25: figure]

File: LWA Ant Meas Proc.docx, Page 5

☐ | Select Cal Kit LWA Ideal Cal Kit 200 MHz Next Port 2 LWA Ideal Cal Kit 200 MHz Finish
☐ | Start Calibration. Follow prompts to Calibrate NA Port 1 and Port 2. Connect and mount each
| Calibration Fixture standard (Open, Short, Load) as prompted
☐ | When the calibration prompts call for connecting Port 1 to Port 2, use an Unknown Thru made
| from a Test Fixture dual assembly that has been split apart and connected back-to-back in-phase
| (A-A, B-B) with spacers. Finish the calibration
☐ | Save/Recall Device Internal (or USB)
☐ | Save/Recall File Type State
☐ | Save/Recall Save Cal_5-200MHz_Date.Time Done
☐ | Leave Test Cables connected to NA
| Diagram 2.1 (Analyzer Calibration for Dipole-Dipole Measurements)

### 2.2. Setup for dipole impedance and dipole-dipole coupling measurements:

10) If desired enable FieldFox internal GPS receiver:
☐ | Connect GPS antenna
☐ | System GNSS (GPS+)
☐ | GNSS Internal (set to Off during idle periods to conserve battery)
☐ | GNSS Settings Display ON Back
11) Connect dipoles:
☐ | Refer to Diagram 2.2 below
☐ | Connect Test Cables to the Antenna Test Fixture and install on Hub of AUT: Test Cable RED to Side
| A and Test Cable GREEN to Side B
☐ | The NA Port 1 already should be connected to Test Cable RED and Port 2 already connected to
| Test Cable GREEN
12) Measure dipoles and save data:
☐ | Save/Recall File Type Data (s2p)
☐ | Save/Recall Save (AN)_DD.MM.YYYY.s2p Done (AN is Antenna Stand Number)
☐ | Save/Recall File Type Picture (PNG)
☐ | Save/Recall Save (AN)_DD.MM.YYYY.png Done
13) Repeat steps 8) through 12) for each additional antenna:

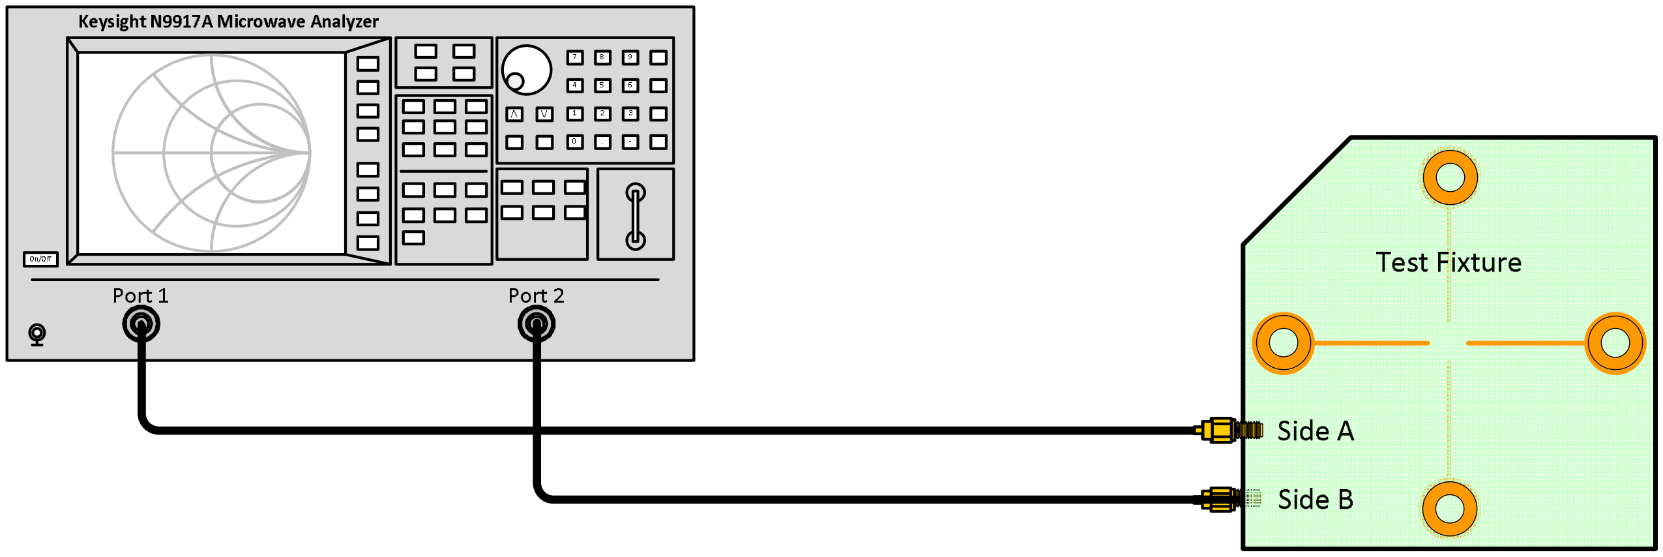
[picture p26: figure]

File: LWA Ant Meas Proc.docx, Page 6

Diagram 2.2 (Dipole Impedance & Dipole-Dipole Measurements)

### 3.0. Antenna-antenna coupling measurements:

a. Antenna-antenna coupling is measured in terms of dB and angle as transmission coefficients S21 and S12.
b. Dipole impedance measurements are incidental to the antenna-antenna coupling measurements. Impedances are measured in terms of dB and angle as reflection coefficients S11 and S22.
c. Four 37 ft (11 m) Test Cables are used to physically isolate the NA from the AUT and also to imitate operational conditions. The cables are placed as close as possible inline with the existing antenna cables.
d. A Full 2-port calibration is used. With the FieldFox, it is necessary to calibrate Port 1 with the Open, Short and Load Calibration Fixtures and then Port 2 with the Open, Short and Load Calibration Fixtures in the specific order shown by the instrument display prompts. An Unknown Thru is used in the last calibration step to connect Port 1 to Port 2.
e. The LWA Ideal Cal Kit 200MHz parameter declarations file (already loaded in the FieldFox NA) is used for network analyzer calibration with the Calibration Fixtures; this calibration file assumes the Calibration Fixtures are ideal (zero coefficients and delay).
f. During calibration and measurements, the Test Cables are connected as follows:
1) One Test Cable is connected between the NA Port 1 and first dipole (A) of the first antenna (X)
2) One Test Cable is connected between a 50 ohm termination and the second dipole (B) of the first antenna (X)
3) One Test Cable is connected between the NA Port 2 and the first dipole (A) of the second antenna (Y)
4) One Test Cable is connected between a 50 ohm termination and the second dipole(B) of the second antenna (Y)
5) Cable connections to the dipoles are swapped at the antennas to enable measurements of the four antenna-antenna coupling combinations: X-A to Y-A; X-A to Y-B; X-B to Y-A; and X-B to Y-B

### 3.1. Setup for calibration of antenna-antenna coupling measurements:

1) Setup Analyzer mode:
☐ Mode NA
2) Setup Traces:
☐ | Trace x4
☐ | Trace 1 Measure S11 Log Mag
☐ | Trace 2 Measure S21 Log Mag

File: LWA Ant Meas Proc.docx, Page 7

☐ | Trace 3 Measure S12 Log Mag
☐ | Trace 4 Measure S22 Log Mag
3) Setup Frequency & display Amplitude:
☐ | Freq/Dist Start 5.0 MHz, Stop 200.0 MHz
☐ | Scale/Amptd Scale 5 dB or 10 dB as required
☐ | Scale/Amptd Ref Level 0 dB
☐ | Scale/Amptd Ref Pos 5
4) Check IF bandwidth and averaging:
☐ | BW IF BW 10 kHz (may require adjustment depending on results, recalibration required)
☐ | BW Average <n> 1 Enter (may require adjustment depending on results)
☐ | BW Average Mode Sweep
☐ | To restart Sweep, go to Sweep Restart
5) Measure setup:
☐ Meas Setup Output power High
6) Setup Sweep:
☐ Sweep Resolution More 1001 Enter Back (resolution 195.0 kHz)
7) Setup Markers:
☐ | Mrkr 1 Normal 5 MHz
☐ | Mrkr 2 Normal 10 MHz
☐ | Mrkr 3 Normal 20 MHz
☐ | Mrkr 4 Normal 40 MHz
☐ | Mrkr 5 Normal 80 MHz
☐ | Mrkr 6 Normal 160 MHz
☐ | Mrkr Table: ON
8) Place cables:
☐ | Place Test Cables as follows:
| Test Cable X-1 (RED) between NA location and Antenna X
| Test Cable X-B (GREEN) between NA location and Antenna X
| Test Cable Y-A (RED-RED) between NA location and Antenna Y
| Test Cable Y-B (GREEN-GREEN) between NA location and Antenna Y
9) Calibrate NA Port 1:
☐ | Refer to Diagram 3.1
☐ | Connect Test Cables as follows.
| Test Cable X-1 (RED) between NA Port 1 and Antenna X Calibration Fixture Side A
| Test Cable X-B (GREEN) between 50 ohm termination and Antenna X Calibration Fixture Side B
| Test Cable Y-A (RED-RED) between NA Port 2 and Antenna Y No Connection
| Test Cable Y-B (GREEN-GREEN) between 50 ohm termination and Antenna Y No Connection
☐ | Cal Mechanical Cal Change DUT Connectors SMA Change Gender Female
| Next Port 2 SMA Change Gender Female Next
☐ | Select Cal Kit LWA Ideal Cal Kit 200 MHz Next Port 2 LWA Ideal Cal Kit 200 MHz Finish

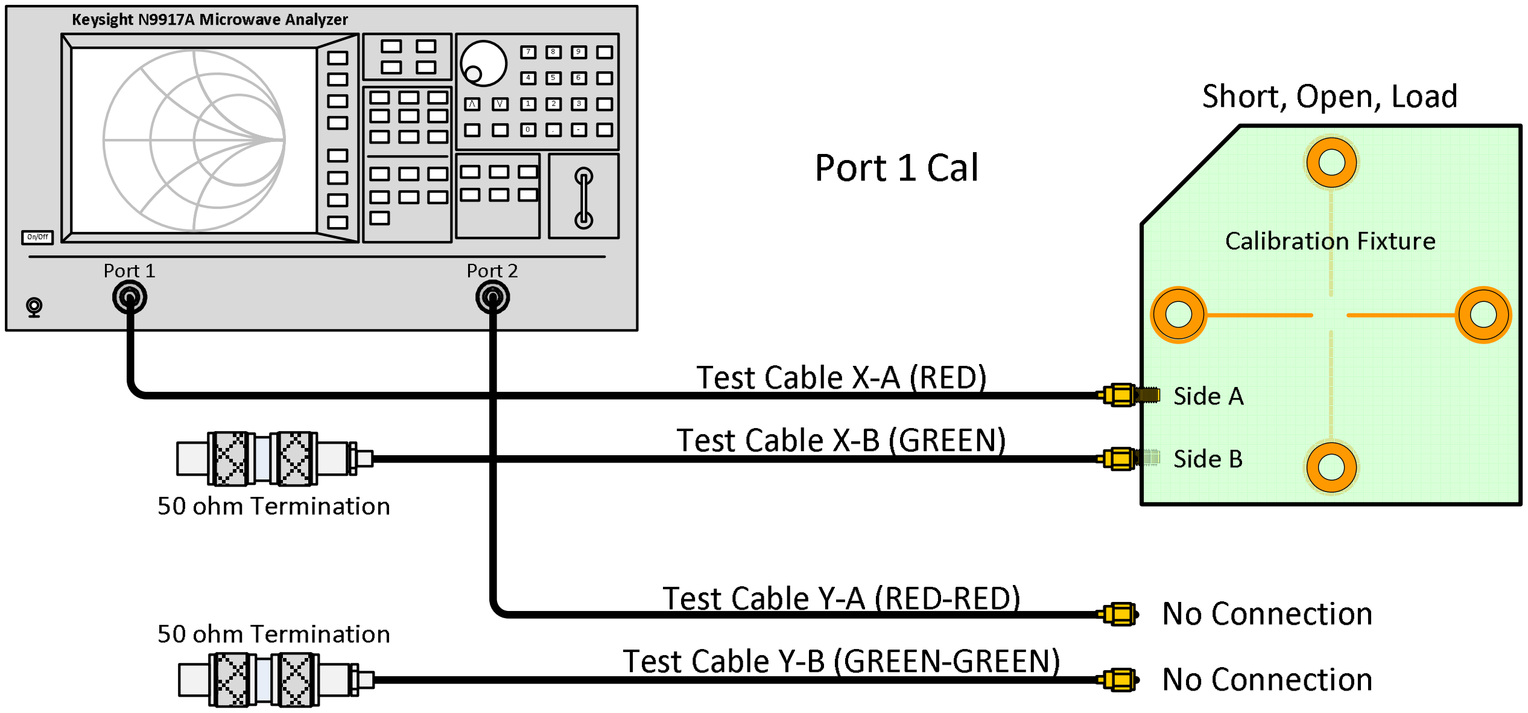
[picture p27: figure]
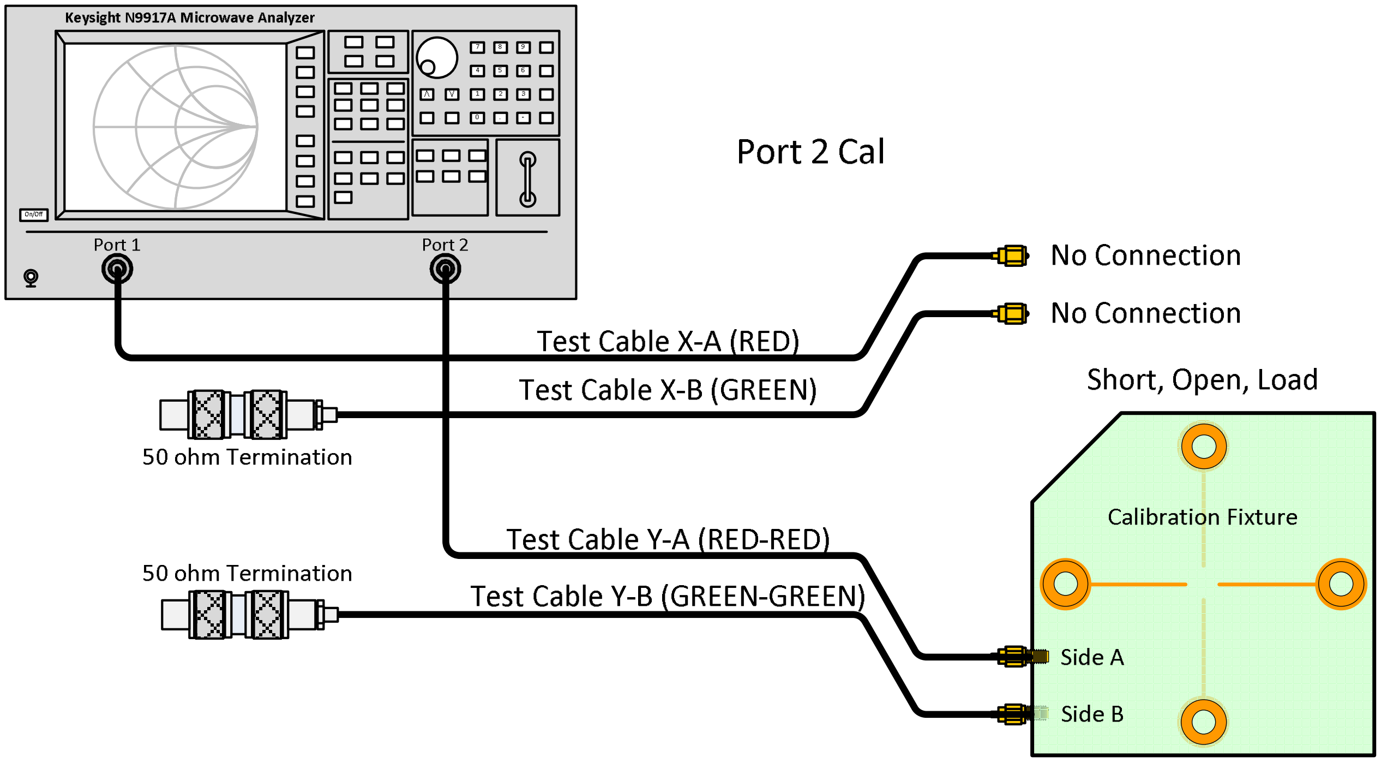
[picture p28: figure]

File: LWA Ant Meas Proc.docx, Page 8

☐ | Start Calibration and follow prompts to Calibrate NA Port 1. Connect and mount each Calibration
| Fixture standard (Open, Short, Load) on the antenna Hub in succession as prompted
☐ | See next step for Port 2 calibration
| Diagram 3.1 (Connections for Port 1 Calibration)
10) Calibrate NA Port 2:
☐ | Refer to Diagram 3.2
☐ | Connect Test Cables as follows
| Test Cable X-1 (RED) between NA Port 1 and Antenna X No Connection
| Test Cable X-2 (GREEN) between 50 ohm termination and Antenna X No Connection
| Test Cable Y-1 (RED-RED) between NA Port 2 and Antenna Y Calibration Fixture Side A
| Test Cable Y-2 (GREEN-GREEN) between 50 ohm termination and Antenna Y Calibration Fixture
| Side B
☐ | Continue Calibration and follow prompts to Calibrate NA Port 2. Connect and mount each
| Calibration Fixture standard (Open, Short, Load) on the antenna Hub in succession as prompted
☐ | See next step for Port 1 to Port 2 Thru calibration
| Diagram 3.2 (Connections for Port 2 Calibration)
11) Calibrate NA Port 1 and Port 2 with Unknown Thru: ☐ Refer Diagram 3.3

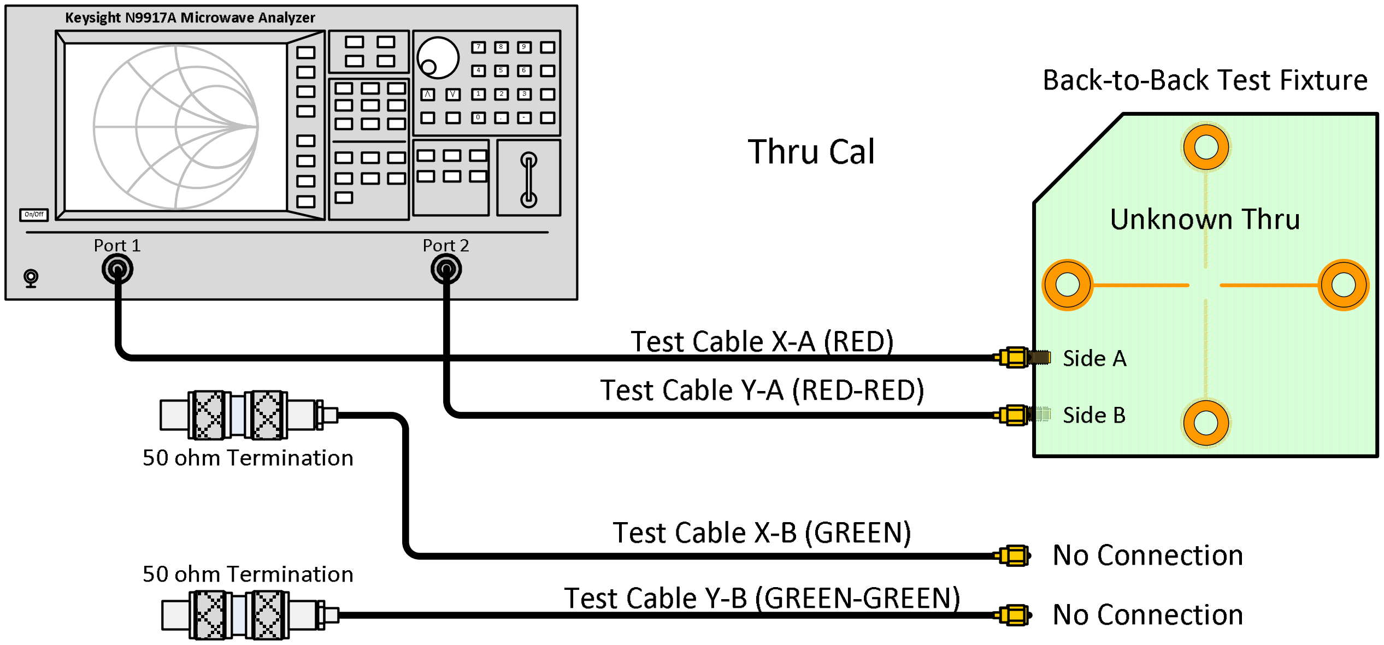
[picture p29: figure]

File: LWA Ant Meas Proc.docx, Page 9

☐ | When the calibration prompts call for connecting Port 1 to Port 2, connect the Test Cables to an
| Unknown Thru made from a Test Fixture dual assembly that has been split apart and connected
| in-phase back-to-back with spacers
☐ | Move the Test Cables so that the ends of both Test Cables are close together
☐ | Connect Test Cables as follows:
| Test Cable X-1 (RED) between NA Port 1 and the Unknown Thru Side A
| Test Cable X-2 (GREEN) between 50 ohm termination and Antenna X No Connection
| Test Cable Y-1 (RED-RED) between NA Port 2 and the Unknown Thru Side B
| Test Cable Y-2 (GREEN-GREEN) between 50 ohm termination and Antenna Y No Connection
☐ | Complete Thru Calibration according to prompts
☐ | Finish the calibration
☐ | Return the ends of the Test Cables to their original locations
| Diagram 3.3 (Connections for Thru Calibration)
12) Save calibration:
☐ | Save/Recall Device Internal (or USB)
☐ | Save/Recall File Type State
☐ | Save/Recall Save Cal_X-Y_5-200MHz_Date.Time Done

### 3.2. Setup for antenna-antenna coupling measurements:

13) If desired, enable internal GPS receiver:
☐ | Connect GPS antenna
☐ | System GNSS (GPS+)
☐ | GNSS Internal (set to Off during idle periods to conserve battery)
☐ | GNSS Settings Display ON Back

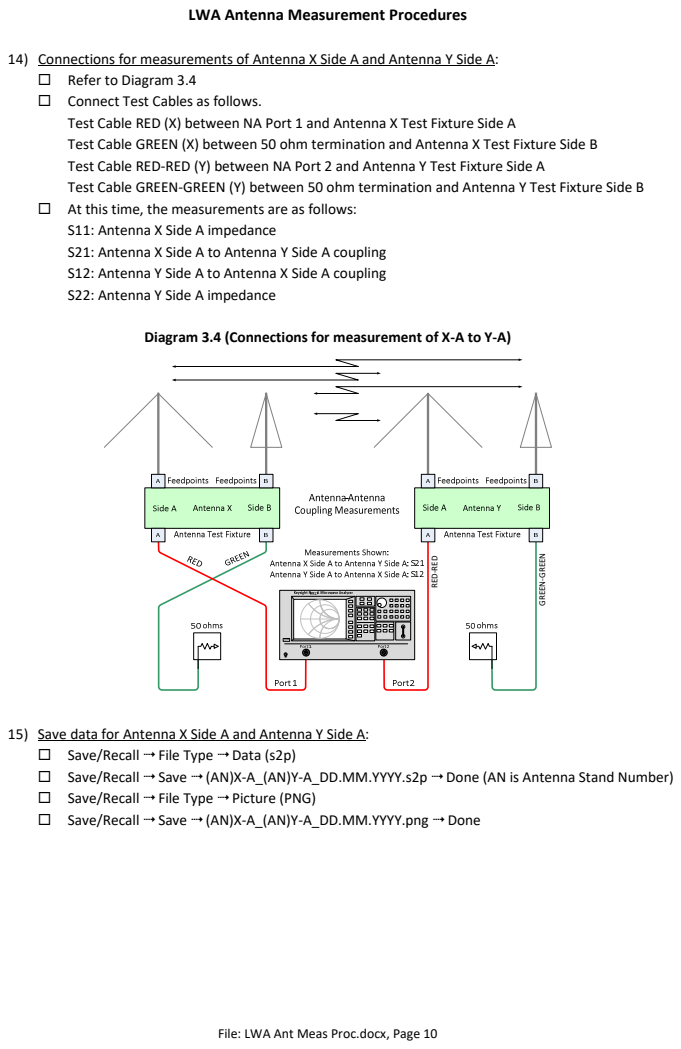
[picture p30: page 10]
Refer to Diagram 3.4; Connect Test Cables as follows.; At this time, the measurements are as follows:; Save/Recall  File Type  Data (s2p); Save/Recall  Save  (AN)X-A_(AN)Y-A_DD.MM.YYYY.s2p  Done (AN is Antenna Stand Number); Save/Recall  File Type  Picture (PNG); Save/Recall  Save  (AN)X-A_(AN)Y-A_DD.MM.YYYY.png  Done; RED-RED; GREEN-GREEN

14) Connections for measurements of Antenna X Side A and Antenna Y Side A:
Test Cable RED (X) between NA Port 1 and Antenna X Test Fixture Side A
Test Cable GREEN (X) between 50 ohm termination and Antenna X Test Fixture Side B
Test Cable RED-RED (Y) between NA Port 2 and Antenna Y Test Fixture Side A
Test Cable GREEN-GREEN (Y) between 50 ohm termination and Antenna Y Test Fixture Side B
S11: Antenna X Side A impedance
S21: Antenna X Side A to Antenna Y Side A coupling
S12: Antenna Y Side A to Antenna X Side A coupling
S22: Antenna Y Side A impedance

Diagram 3.4 (Connections for measurement of X-A to Y-A)

15) Save data for Antenna X Side A and Antenna Y Side A:

File: LWA Ant Meas Proc.docx, Page 10

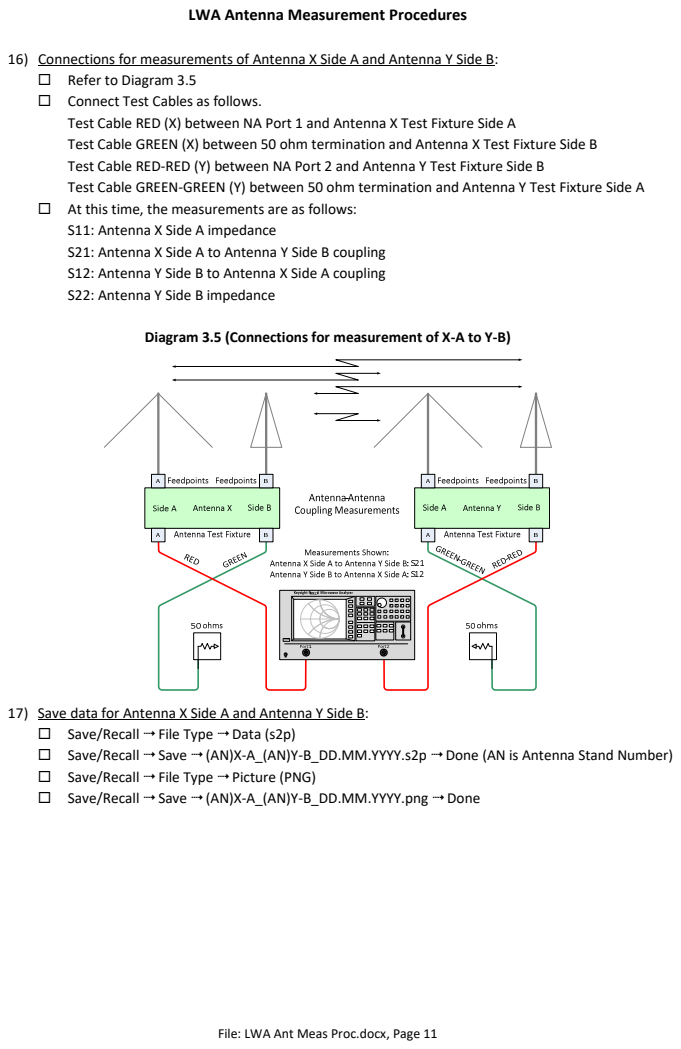
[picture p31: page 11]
Refer to Diagram 3.5; Connect Test Cables as follows.; At this time, the measurements are as follows:; Save/Recall  File Type  Data (s2p); Save/Recall  Save  (AN)X-A_(AN)Y-B_DD.MM.YYYY.s2p  Done (AN is Antenna Stand Number); Save/Recall  File Type  Picture (PNG); Save/Recall  Save  (AN)X-A_(AN)Y-B_DD.MM.YYYY.png  Done

16) Connections for measurements of Antenna X Side A and Antenna Y Side B:
Test Cable RED (X) between NA Port 1 and Antenna X Test Fixture Side A
Test Cable GREEN (X) between 50 ohm termination and Antenna X Test Fixture Side B
Test Cable RED-RED (Y) between NA Port 2 and Antenna Y Test Fixture Side B
Test Cable GREEN-GREEN (Y) between 50 ohm termination and Antenna Y Test Fixture Side A
S11: Antenna X Side A impedance
S21: Antenna X Side A to Antenna Y Side B coupling
S12: Antenna Y Side B to Antenna X Side A coupling
S22: Antenna Y Side B impedance

Diagram 3.5 (Connections for measurement of X-A to Y-B)

17) Save data for Antenna X Side A and Antenna Y Side B:

File: LWA Ant Meas Proc.docx, Page 11

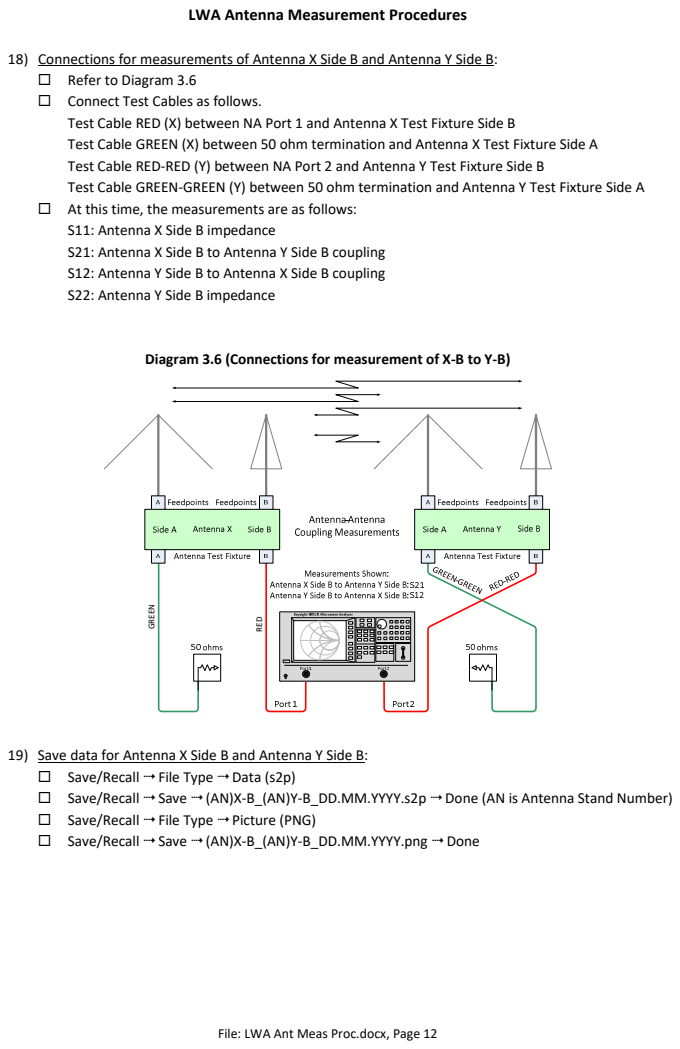
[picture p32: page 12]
Refer to Diagram 3.6; Connect Test Cables as follows.; At this time, the measurements are as follows:; Save/Recall  File Type  Data (s2p); Save/Recall  Save  (AN)X-B_(AN)Y-B_DD.MM.YYYY.s2p  Done (AN is Antenna Stand Number); Save/Recall  File Type  Picture (PNG); Save/Recall  Save  (AN)X-B_(AN)Y-B_DD.MM.YYYY.png  Done; GREEN; RED

18) Connections for measurements of Antenna X Side B and Antenna Y Side B:
Test Cable RED (X) between NA Port 1 and Antenna X Test Fixture Side B
Test Cable GREEN (X) between 50 ohm termination and Antenna X Test Fixture Side A
Test Cable RED-RED (Y) between NA Port 2 and Antenna Y Test Fixture Side B
Test Cable GREEN-GREEN (Y) between 50 ohm termination and Antenna Y Test Fixture Side A
S11: Antenna X Side B impedance
S21: Antenna X Side B to Antenna Y Side B coupling
S12: Antenna Y Side B to Antenna X Side B coupling
S22: Antenna Y Side B impedance

Diagram 3.6 (Connections for measurement of X-B to Y-B)

19) Save data for Antenna X Side B and Antenna Y Side B:

File: LWA Ant Meas Proc.docx, Page 12

Refer to Diagram 3.7; Connect Test Cables as follows.; At this time, the measurements are as follows:; Save/Recall  File Type  Data (s2p); Save/Recall  Save  (AN)X-B_(AN)Y-A_DD.MM.YYYY.s2p  Done (AN is Antenna Stand Number); Save/Recall  File Type  Picture (PNG); Save/Recall  Save  (AN)X-B_(AN)Y-A_DD.MM.YYYY.png  Done; 22) Repeat steps 8) through 21) for each additional antenna pair GREEN; RED; RED-RED; GREEN0-GREEN

20) Connections for measurements of Antenna X Side B and Antenna Y Side A:
Test Cable RED (X) between NA Port 1 and Antenna X Test Fixture Side B
Test Cable GREEN (X) between 50 ohm termination and Antenna X Test Fixture Side A
Test Cable RED-RED (Y) between NA Port 2 and Antenna Y Test Fixture Side A
Test Cable GREEN (Y) between 50 ohm termination and Antenna Y Test Fixture Side B
S11: Antenna X Side B impedance
S21: Antenna X Side B to Antenna Y Side A coupling
S12: Antenna Y Side A to Antenna X Side B coupling
S22: Antenna Y Side A impedance

Diagram 3.7 (Connections for measurement of X-B to Y-A)

21) Save data for Antenna X Side B and Antenna Y Side A:

File: LWA Ant Meas Proc.docx, Page 13

File: LWA Ant Meas Proc.docx, Page 14

Document Information
Authors: Whitham D. Reeve
Revisions: 0.0 (Original draft derived from measurements report produced summer 2022, 26 Sep 2022)
| 0.1 (Completed 1st Draft, 1 Oct 2022)
| 0.2 (Revised dipole-dipole and antenna-antenna steps, 08 Oct 2022) 0.3 (Added Unknown Thru to calibrations and illustrations, 09 Oct 2022) 0.4 (Completed 2nd Draft, 12 Oct 2022)
| 0.5 (Revised cable designations, 15 Oct 2022)

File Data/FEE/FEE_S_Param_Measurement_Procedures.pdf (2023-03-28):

FEE S-Parameter Measurement Procedures with FEE Test Fixture V2

File: CMT FEE S-Param Meas Proc V2.docx, Page 1

### 0. General:

a. These procedures describe FEE S-Parameter measurements using the Copper Mountain Technologies M5045 VNA, custom Calibration Fixtures and a commercial mechanical Calibration Kit, and custom FEE Test Fixture version 2. A block diagram of the FEE Test Fixture is in section 1.
b. The custom Calibration Fixtures are used to calibrate the VNA Port 1. The hybrid coupler on the FEE Test Fixture Coupler PCB is de-embedded during VNA calibration by using the custom Calibration Fixtures and associated Data-Base Standards.
1) The Calibration Fixtures are version 2 with the MCL AMT-32+ 180° hybrid coupler. These hybrid couplers are identical to the hybrid coupler on the Coupler PCB in the upper bay of the FEE Test Fixture V2.
2) Two Calibration Fixtures are used, one for calibrating the A-side and one for calibrating the B-side prior to measuring the A- and B-sides of the FEE. The only difference in the A- and B-sides of the Calibration Fixtures is the direction of the RF connector on the PCB. The Calibration Fixture A- and B-side PCBs are sandwiched together in the same manner as the FEE A- and B- side PCBs.
3) The custom Calibration Fixtures are defined in the VNA software using Data-Based Calibration Standards produced from previous S-Parameter measurements of the fixtures after the VNA and associated test cables had been calibrated with an Automatic Calibration Module.
c. The commercial Calibration Kit is used to calibrate the VNA Port 2. The bias-tee and associated cables in the lower bay of the FEE Test Fixture V2 are de-embedded during calibration using the commercial Calibration Kit and two short proxy cables. The proxy cables are identical to those used in the FEE Test Fixture V2 lower bay. Disassembling the FEE Test Fixture is avoided by using proxy cables.
d. Dual assembly FEEs are mounted using all four studs (feedpoints) in the FEE Test Fixture, but only one side is measured at a time. For reference, FEE Side-A is the side facing up and FEE Side-B is the side facing down when mounted in the Test Fixture.
e. The 30 dB attenuator on the FEE Test Fixture RF Input, if equipped, is removed and not reconnected until all measurements are completed. This attenuator is used only when a spectrum analyzer with tracking generator is used to measure FEE gain.
f. The measurement frequency range is 5 to 200 MHz.

File: CMT FEE S-Param Meas Proc V2.docx, Page 2

### 1.1. Preliminary:

a. Test equipment:
1) FEE Test Fixture V2 (equipped with MCL AMT-32+ on Coupler PCB) , custom built. This test fixture includes one MCL 141-6SMRSM+ Internal Input Jumper Cable and one Bracke 92306.12 (RG-188D) Internal Output Jumper Cable, both cables in the upper bay
2) Calibration Fixtures V2, Open, Short, and Load, custom built, Yellow-A and Yellow-B designations
3) Calibration Kit, SMA or 3.5 mm Female (see c. below)
4) Copper Mountain Technologies M5045 vector network analyzer (see c. below)
5) Test cables, 1 m long, SMA-M : N-M, MCL ULC-1M-SMNM+, 2 required (marked Red & Green)
6) Jumper Cable, 6 in long, MCL 141-6SMRSM+ (proxy Input Jumper Cable)
7) Jumper Cable, 12 in long, Bracke 92306.12 (RG-188D) (proxy Output Jumper Cable)
8) Coupler, SMA-Female-Female, Bulkhead type (2 required for proxy cables)
9) Torque wrench, 5/16 in (8 mm), Pre-set to 5 in-lbs (0.56 N-m)
b. Test set status as of 23 February 2023:
Mfr | Type | S/N | Cal due
CMT | Compact M5045 VNA, SW 22.4.3 | 22160017 | 15 Jul 2024
MCL | KSOLT-63-S+ SMA Calibration Kit | 2230-007 (Female) | 9 Sep 2024

### 1.2. S-Parameter Measurements:

a. These procedures measure all four S-Parameters of the FEE: S11, S21, S12, S22.
b. The VNA ports are calibrated using 2-Port SOLT procedures with output power set to 0 dBm. The output power is then reduced to –35 dBm (Port 1) and –25 dBm (Port 2) for subsequent FEE measurements. The Port 1 power level provides an optimum VNA receiver input level (after amplification by the FEE) for S11 measurements and a 16.5 dB margin below the 1 dB output compression level of the FEE. The Port 2 output level is chosen as a compromise between low reverse power into active circuits and VNA trace noise.
c. To compensate for the reduced dynamic range when the VNA output power is reduced, the IF bandwidth is reduced to 1 kHz (from 10 kHz default) prior to VNA calibration. Moderate sweep averaging is used to reduce trace noise.
d. The S-Parameters are measured for both sides (A & B) of each FEE. This requires recalibrating the VNA and reconnecting the FEE in the FEE Test Fixture for each side. Recalibrations and reconnections are minimized by measuring all Side-As and then all Side-Bs of the FEEs under test.
e. The VNA is calibrated at the beginning of each measurement day. It is recalibrated if any of the following are changed after initial calibration: Frequency range; IF Bandwidth; Resolution; and Lab temperature by more than 5 °C. Notes: 1) These procedures do not require changing any of these settings, and the lab temperature and humidity are stable during the day; 2) Output powers of the CMT VNA ports can be changed without affecting calibration.
f. All FEEs have a serial number indicated in the filename when saving the measurements.

File: CMT FEE S-Param Meas Proc V2.docx, Page 3

### 1.3. Setup:

a. FEE Test Fixture V2:

☐ Set FEE Test Fixture switches for Internal Power and turn OFF

b. System setup:

☐ Preset OK

c. Stimulus setup:
☐ | Start 5.0 MHz, Stop 200.0 MHz
☐ | Points 1001
☐ | Sweep type Lin Freq
☐ | IF Bandwidth 1 kHz
☐ | Port Couple Off
d. Display setup:
☐ | Allocate Channels x1
☐ | Number of Traces 4
☐ | Allocate Traces x1
e. Markers:
☐ | Markers Add Marker 5M, 10M, 20M, 40M, 80M, 160M
☐ | Marker Properties (Defaults)
f. Connections for analyzer calibration:
☐ | Refer to Diagram 1.3.1 below
☐ | Connect VNA Port 1 to Side A of the Calibration Fixtures through Test Cable 1 and proxy Input
Jumper Cable (MCL 141-6SMRSM) through an SMA-Female coupler
☐ | Connect VNA Port 2 to the FEE Test Fixture RF Output connector through Test Cable 2.
☐ | Temporarily disconnect the 75 mm Interbay Jumper Cable from the FEE Test Fixture RF Output + dc
connector and connect to the proxy Output Jumper Cable (Bracke 92306.12) through an SMA-Female coupler
g. Calibration:
☐ | Stimulus Port Power Port 1 0 dBm Port 2 0 dBm
☐ | Averaging On
☐ | Average Factor 10 (default)
☐ | Smoothing Off (default)
☐ | Calibration Select the Yellow Side-A Calibration Kit Combo from the Cal Kit list: Calibration Cal
Kit LWA_Yel-A_C Select
☐ | Calibrate 2-Port SOLT Cal
☐ | Start Calibration, connect the calibration devices to calibrate the VNA ports:
☐ | Port1 Open (PCB Open Yel A) Port1 Short (PCB Short Yel A) Port1 Load (PCB Load Yel A)
☐ | Port2 Open (Open SMA-F) Port2 Short (Short SMA-F) Port2 Load (Load SMA-F)
☐ | Port1-2 Thru (BackToBack)

File: CMT FEE S-Param Meas Proc V2.docx, Page 4

☐ | Apply (check Cor field in left side of Status Bar)
☐ | Save/Recall Save Type State & Cal
☐ | Save State File Cal_5-200MHz_Date.Time
☐ | Averaging Off
☐ | Remove the proxy Input Jumper Cable from the Test Cable 1 and connect Test Cable 1 to the FEE
| Test Fixture RF Input
☐ | Remove the proxy Output Jumper Cable from the 75 mm Interbay Jumper Cable and reconnect the
| Interbay Jumper Cable to the RF Output + dc connector on the FEE Test Fixture
h. Reduce Port 1 output power:

☐ Stimulus Power Port Power Port 1 –35 dBm Port 2 –25 dBm

i. Connections for FEE measurements:
☐ | Check that FEE Test Fixture power is OFF
☐ | Refer to Diagram 1.3.2 below and connect the FEE side A (B) to the internal RF Output Cable
☐ | Install the FEE in the FEE Test Fixture using all four studs
j. Measure FEE as DUT and save data:
☐ | Turn ON FEE Test Fixture power
☐ | Average Factor 20 (or as necessary to reduce trace noise)
☐ | Averaging On
☐ | After Averaging completes, Save/Recall Save Data to Touchstone File 2 Port (s2p) Format
| dB-Angle
☐ | Save File Filename SNxxxx-A(B)_Date.Time.s2p
☐ | System Print Print Color Color Invert Image Print Date & Time Print to File
☐ | Save File Filename SNxxxx-A(B)_Date.Time.png
☐ | Averaging Off
☐ | Turn OFF FEE Test Fixture power and prepare to measure Side A of the next FEE
☐ | Repeat Side A measurements of all FEEs from beginning of step i.
k. FEE Side B measurements:
☐ | Calibrate Side B using step g. and h. except select the Yellow Side-B Calibration Kit Combo from the
| Cal Kit list: Calibration Cal Kit LWA_Yel-B_C Select
☐ | Repeat Side B measurements of all FEEs from beginning of step i.

Port 2Port 1; VVS; Test Cable 1; FEE; 180° Hybrid Coupler; Bracke 92306.12 RG-188D; RF Output + dc; RF Input + dc; RF + dcRF; RF Input; RF Output; D OUT; DUT; 15 Vdc Power Supply; Coupler PCB; Port 1 Reference Plane; Test Cable 2; Calibration Fixture; Proxy Input Jumper Cable; Proxy Output Jumper Cable; Port 2 Reference Plane; Proxy SMA-F Coupler; UNKNOWN THRU; Input Jumper Cable; OPEN SHORT LOAD

Diagram 1.3.1 (Analyzer Calibration)

Test Fixture PCB 1

Test Fixture PCB 2

MCL Hand-Flex
141-6SMRSM+

Vector Network Analyzer

Output Jumper
Cable
FEE Test Fixture
~ Upper Bay

086-12SBSM+

MCL Bias-Tee
ZFBT-4R2GW

Internal Power Supply Selected
and Off during calibration

~ Lower Bay

Diagram 1.3.2 (FEE S-Parameter Measurement)

File: CMT FEE S-Param Meas Proc V2.docx, Page 5

File: CMT FEE S-Param Meas Proc V2.docx, Page 6

Document Information
Author: Whitham D. Reeve
Revisions: 0.0 (Original draft started based on V1 procedures, 28 Dec 2022) 0.1 (First pass thru procedures, 02 Jan 2023)
0.2 (Revised, 18 Jan 2023)
0.3 (Minor edits, 20 Jan 2023)
0.4 (Calibration revisions based on Zoom call with Brian Walker, Copper Mountain Tech., 23 Feb 2023) 0.5 (Cleanup based on dry run, 24 Feb 2023)
0.6 (Record for V1.8 and V2.0 measurements, 26 & 27 Feb 2023)

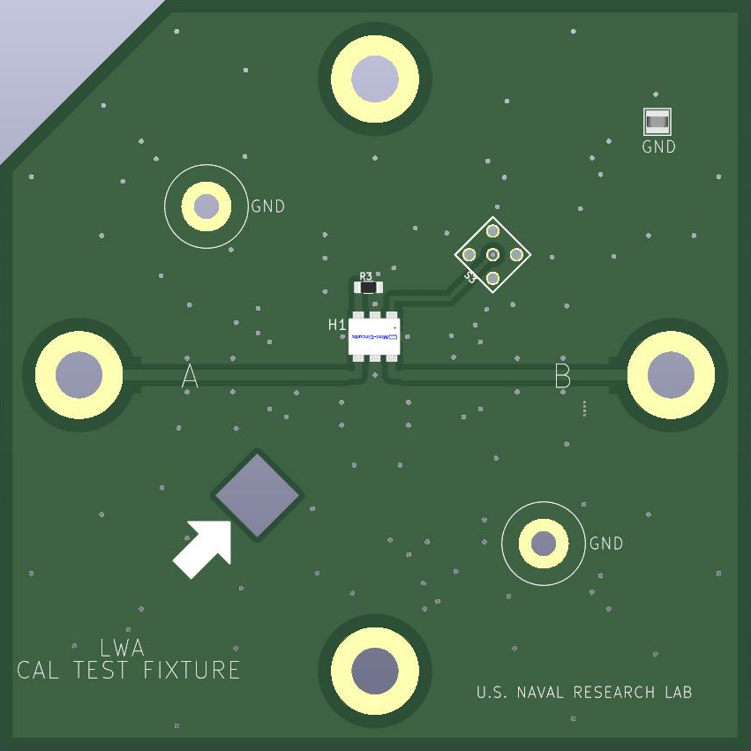
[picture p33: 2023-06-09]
Test Fixtures/LWA Active Test Fixture 2022/JPG Image Files/Test_Fixture v2.jpg

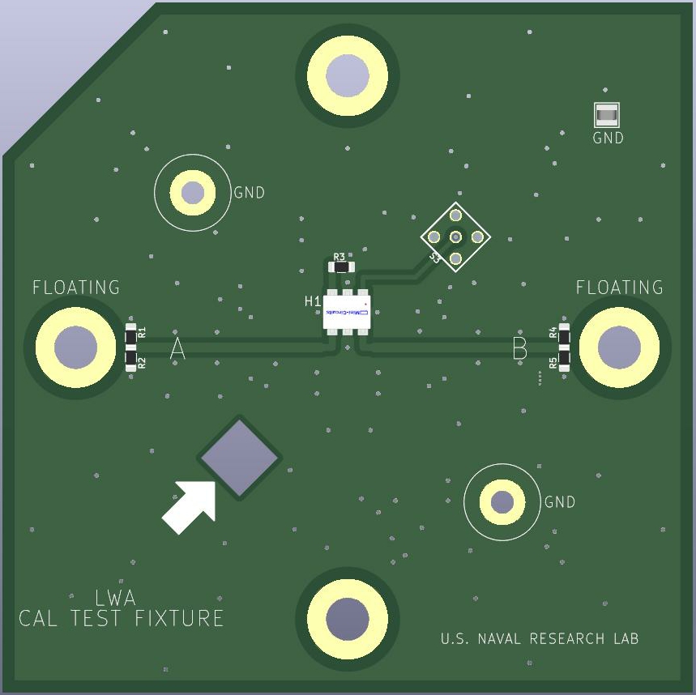
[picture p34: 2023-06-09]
Test Fixtures/LWA Cal Test Fixture 2022/JPG Image Files/Cal_Fixture v2.jpg

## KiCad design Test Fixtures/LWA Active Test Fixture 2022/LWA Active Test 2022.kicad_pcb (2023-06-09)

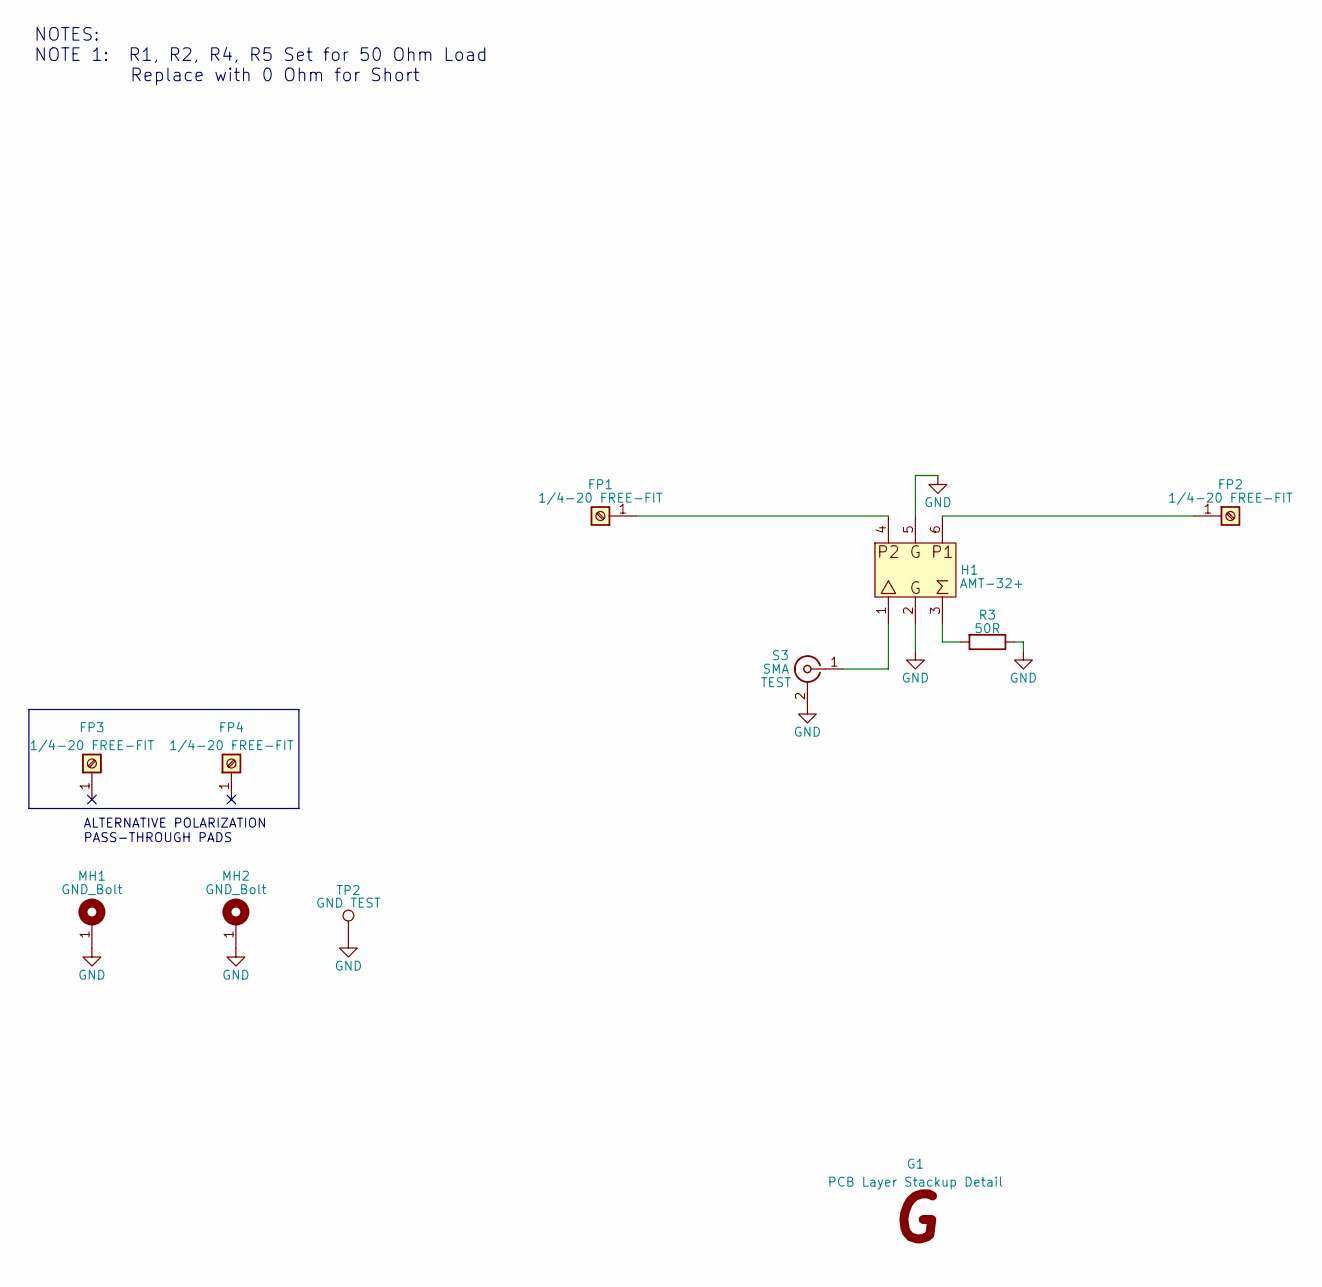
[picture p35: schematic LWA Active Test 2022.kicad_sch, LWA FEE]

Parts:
FP1, FP2, FP3, FP4: 1/4-20 FREE-FIT; Feedpoint; Tolerance NA; Voltage Rating NA; MPN DNI
G1: PCB Layer Stackup Detail; FabDrawing-2Layer-Imperial_LWA
H1: AMT-32+; AMT-2; Tolerance NA; Voltage Rating NA; MPN AMT-32+
MH1, MH2: GND_Bolt
R3: 50R; R_1206_3216Metric_Pad1.30x1.75mm_HandSolder; Tolerance 0.1%; Voltage Rating NA; MPN Y162550R0000B9W
S3: TEST; SMA_142-0701-201; Tolerance NA; Voltage Rating NA; MPN 142-0701-201
TP2: GND TEST; Harwin_TP_S1751-46R; Tolerance NA; Voltage Rating NA; MPN S1751-46R

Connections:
GND: H1.2, H1.5, MH1.1, MH2.1, R3.1, S3.2 (Ext), TP2.1
unnamed: FP1.1, H1.4
unnamed: H1.1, S3.1 (In)
unnamed: H1.3, R3.2
unnamed: FP2.1, H1.6

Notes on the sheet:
NOTES: NOTE 1: R1, R2, R4, R5 Set for 50 Ohm Load Replace with 0 Ohm for Short
ALTERNATIVE POLARIZATION PASS-THROUGH PADS

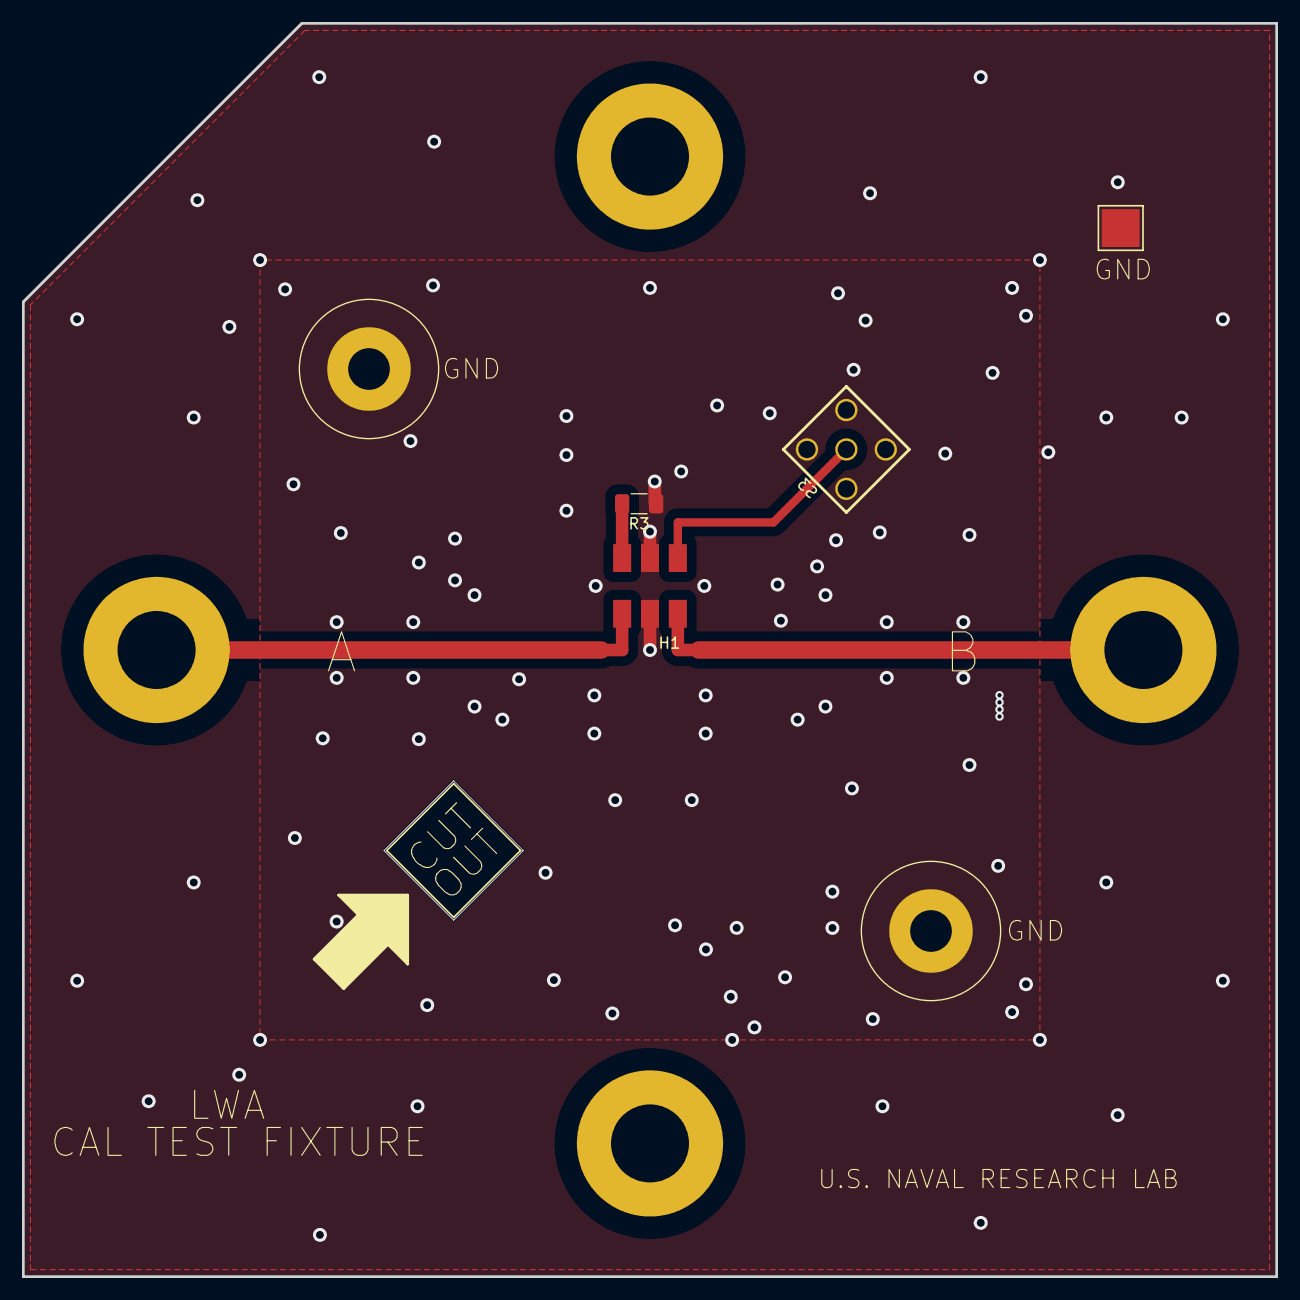
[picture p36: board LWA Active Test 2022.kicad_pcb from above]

Board: 2 copper layers, 114.3 x 114.3 mm, 11 parts (1 on the bottom side), 5 nets.

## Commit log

2022-11-22 Removed unneccesary print statement
2023-01-17 Changed FEE gain to voltage gain for consistency. Added convenience plotting script to quickly plot FEE gain.
2023-01-23 Forgot to stage changes to comoute_IMF.py for commit
2023-05-24 Added KiCAD files for the test/calibration fixtures and the v2 FEE board.
    [0ZCJ0050AF2E.STEP, 142-0701-201.stp, 2035-09-sm-rplf.stp, 459120007.stp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]
2023-06-09 The FEE now has its own repo.
    [0ZCJ0050AF2E.STEP, 142-0701-201.stp, 2035-09-sm-rplf.stp, 459120007.stp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]
2023-06-09 Move KiBOM over to a submodule.
    [kibom-test.kicad_pcb, kibom-test.sch]

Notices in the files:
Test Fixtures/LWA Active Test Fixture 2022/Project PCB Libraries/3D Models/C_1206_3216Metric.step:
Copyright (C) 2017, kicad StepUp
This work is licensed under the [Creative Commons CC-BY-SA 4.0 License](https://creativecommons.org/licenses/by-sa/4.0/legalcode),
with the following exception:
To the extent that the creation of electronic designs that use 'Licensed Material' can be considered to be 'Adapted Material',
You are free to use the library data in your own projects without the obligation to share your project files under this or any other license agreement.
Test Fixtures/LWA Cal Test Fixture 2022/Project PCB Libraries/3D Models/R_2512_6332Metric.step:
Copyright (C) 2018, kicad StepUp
